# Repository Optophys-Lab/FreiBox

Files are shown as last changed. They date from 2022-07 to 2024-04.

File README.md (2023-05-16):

# FreiBox
Open-ressource for building FreiBox and its modules (including FreiBox Active Commutator).
It contains codes, references tables for electronic components, 3D stl files and pictures.

Contact:
Brice De La Crompe,
brice . de . la . crompe /at/ biologie . uni-freiburg . de,
Optophysiology Lab (Ilka Diester's lab),
Freiburg, Germany

For specific question regarding the GUI, please contact:
megan . j . schneck /at/ gmail . com

______________________
Component Overview
______________________

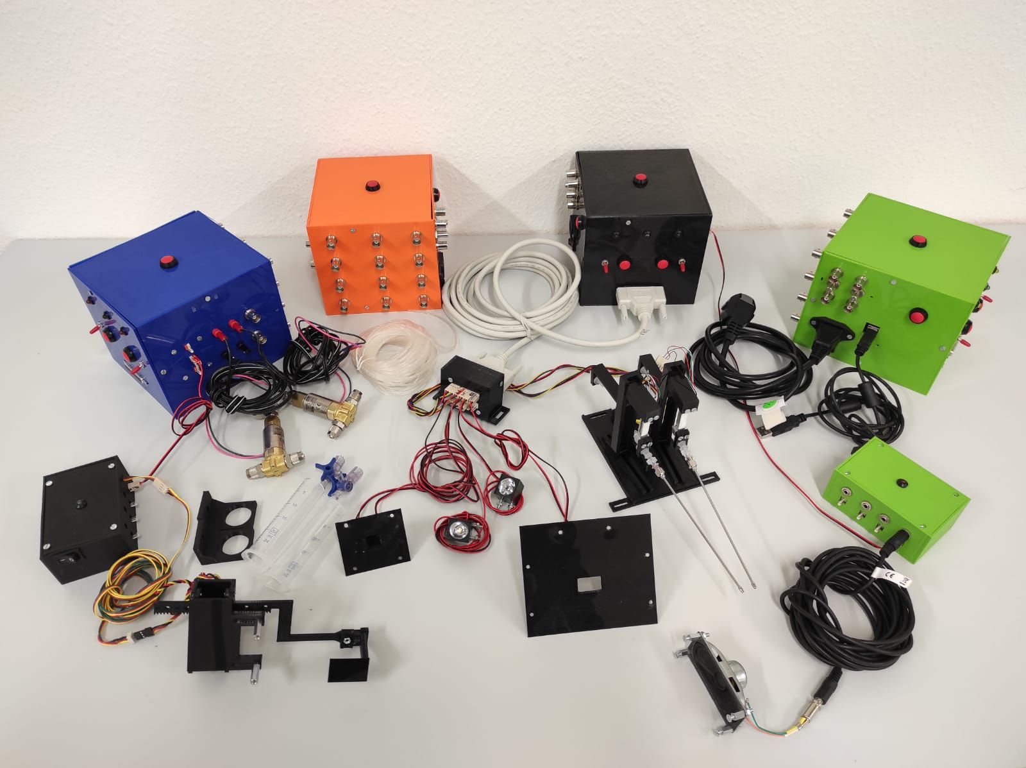
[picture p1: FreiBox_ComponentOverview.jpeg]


______________________
Licking Chamber
______________________

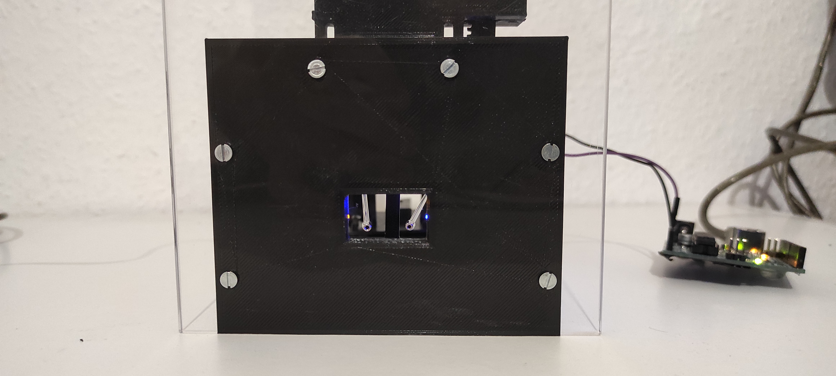
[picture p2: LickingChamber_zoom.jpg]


______________________
Lickometer in action
______________________

LickingRecordingExample_Compressed.mp4

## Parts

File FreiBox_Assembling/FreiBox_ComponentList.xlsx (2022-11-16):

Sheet: Total
Table1: Freibox plateform
ID | Name | Price
1 | Freibox | 902.8118
2 | Commutator | 110.74
3 | Tools | 160.4
4 | Miniscope UCLA v4 | 1580
5 | Open ephys system | 3479
6 | Laser Controler | 900
7 | Computer | 1500
 | Total | 8632.9518
Miniscope UCLA v4
ID | Name | Comment | Quantity | Reference | Supplier | Supplier ref | Price (incl. taxes) | All Price (incl. taxes)
1 | Miniscope V4 Assembly Kit |  | 1 |  | Open ephys |  | 1095 | 1095
2 | New DAQ v3.3 |  | 1 |  | Open ephys |  | 350 | 350
3 | Miniscope V4 Base Plate (Variant 2) |  | 1 |  | Open ephys |  | 35 | 35
4 | Miniscope V4 Coax Cable |  | 1 |  | Open ephys |  | 100 | 100
 |  |  |  |  |  |  | Total | 1580
Open ephys system
ID | Name | Comment | Quantity | Reference | Supplier | Supplier ref | Price (incl. taxes) | All Price (incl. taxes)
1 | Acquisition Board |  | 1 |  | Open ephys |  | 2464 | 2464 | 740
2 | I/O Board |  | 1 |  | Open ephys |  | 85 | 85
3 | RHD 16-channel headstage |  | 1 | Intan/C3334 | Intan |  | 720 | 720
4 | RHD 3-ft (0.9 m) standard SPI interface cable |  | 1 | Intan/C3203 | Intan |  | 210 | 210
 |  |  |  |  |  |  | Total | 3479
Laser Controler
ID | Name | Comment | Quantity | Reference | Supplier | Supplier ref | Price (incl. taxes) | All Price (incl. taxes)
1 | Pulse Pal v2 |  | 1 | Sanworks/1102 |  |  | 900 | 900
 |  |  |  |  |  |  | Total | 900

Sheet: FreiBox
Licking detection |  |  |  |  |  |  |  |  | Categories | Price | Quantities | Total
ID | Name | Comments | Quantity | Reference | Supplier | Supplier ref | Price (incl. taxes) | All Price (incl. taxes) | Licking detection | 44.1 | 2 | 88.2
1 | Strain gauge (load cell, 100G) |  | 2 | SparkFun/SEN-14727 | Digikey | 1568-1898-ND | 12.5 | 25 | Head entry detection | 9.08 | 2 | 18.16
2 | Strain gauge instrumental amplifier |  | 2 | Texas Instruments/INA125PA | Digikey | INA125PA-ND | 7.5 | 15 | Licking signal conditioning | 12.17 | 2 | 24.34
3 | Trimmer 100Ω 0.5W (20 turns) | to set amplifcation gain of the Strain gauge instrumental amplifier | 2 | TTE/67YR100LF | Digikey | 987-1502-ND | 2.05 | 4.1 | Voltage comparator | 3.01 | 4 | 12.04
4 | Ceramic capacitor 100nF |  | 2 | AVX/SR205E104MAR | RS | 144-1933 | 0.5 | 1 | Voltage reference for licking detection module | 40.8 | 2 | 81.6
 |  |  |  |  |  |  |  |  | Voltage reference for Head detection module | 2 | 2 | 4
 |  |  |  |  |  |  | subtotal | 44.1 | Water delivery | 29.86 | 2 | 59.72
 |  |  |  |  |  |  |  |  | Manual water delivery module | 8.58 | 2 | 17.16
Head entry detection |  |  |  |  |  |  |  |  | Light Module | 3.19 | 2 | 6.38
ID | Name | Comments | Quantity | Reference | Supplier | Supplier ref | Price (incl. taxes) | All Price (incl. taxes) | Behavioral Box accessories | 61.1148 | 1 | 61.1148
5 | IR emitting LED |  | 1 | TTE/OP132 | Digikey | 365-1041-ND | 3.25 | 3.25 | Audio pure tone generator | 30.26 | 1 | 30.26
6 | IR receiver phototransistor |  | 1 | Osram/BPX43-4/5 | Digikey | 475-2660-ND | 5.4 | 5.4 | Optoisolated Gate control circuit | 48.55 | 1 | 48.55
7 | Resistor 100Ω ±1% |  | 1 | Vishay/MBB02070C1000FCT00 | RS | 477-7681 | 0.35 | 0.35 | Powering | 45.022 | 1 | 45.022
8 | Resistor 100KΩ ±1% |  | 1 | TE Connectivity/ LR1F100K | RS | 171-1691 | 0.08 | 0.08 | Arduino and accessories | 145.9 | 1 | 145.9
 |  |  |  |  |  |  |  |  | Inside Box | 13.94 | 1 | 13.94
 |  |  |  |  |  |  |  |  | Mechanical parts | 45.04 | 1 | 45.04
 |  |  |  |  |  |  | subtotal | 9.08 | Connectors | 59.9 | 1 | 59.9
 |  |  |  |  |  |  |  |  | Plexiglas box | 77 | 1 | 77
Licking signal conditioning |  |  |  |  |  |  |  |  | 3D printing | 64.485 | 1 | 64.485
ID | Name | Comments | Quantity | Reference | Supplier | Supplier ref | Price (incl. taxes) | All Price (incl. taxes) |  |  | Total | 902.8118
9 | High speed operational amplifier | To divide the licking signal and limit the output to [-5V; +5V] | 2 | Texas Instruments/LM7171BIN/NOPB | Digikey | LM7171BIN/NOPB | 4.8 | 9.6
10 | Resistor 5kΩ ±1% |  | 1 | Vishay/MBB0207VD5001BC100 | Digikey | BC4514CT-ND | 0.75 | 0.75
11 | Resistor 1.5kΩ ±1% |  | 1 | Tru components/1557396 | Conrad | 1557396 - VQ | 0.07 | 0.07
12 | Resistor 100Ω ±1% |  | 1 | Vishay/MBB02070C1000FCT00 | RS | 477-7681 | 0.35 | 0.35
13 | Zener limiting diode (5.1V) | Limiting diode for licking signal divider. Limit output to [-5V; +5V] | 2 | Vishay/BZX85C5V1-TR | Conrad | 180572 | 0.2 | 0.4
14 | Ceramic capacitor 100nF |  | 2 | AVX/SR205E104MAR | RS | 144-1933 | 0.5 | 1
 |  |  |  |  |  |  | subtotal | 12.17
Voltage comparator
ID | Name | Comments | Quantity | Reference | Supplier | Supplier ref | Price (incl. taxes) | All Price (incl. taxes)
15 | Differential comparator |  | 1 | Texas Instruments/LM311P | Digikey | 296-1389-5-ND | 0.65 | 0.65
16 | Ceramic capacitor 2.2nF |  | 1 | Tru components/TC-K2,2NF5 | Conrad | 1589521 | 0.09 | 0.09
17 | Resistor 100Ω ±1% |  | 1 | Vishay/MBB02070C1000FCT00 | RS | 477-7681 | 0.35 | 0.35
18 | Resistor 1MΩ ±1% |  | 1 | Yageo/MF0207F1M0H | Conrad | 1417625 | 0.13 | 0.13
19 | Resistor 470KΩ ±1% |  | 1 | Yageo/MF0207F470KH | Conrad | 1417688 - 62 | 0.04 | 0.04
20 | Resistor 5kΩ ±1% | Pull-up resistor | 1 | Vishay/MBB0207VD5001BC100 | Digikey | BC4514CT-ND | 0.75 | 0.75
21 | Ceramic capacitor 100nF |  | 2 | AVX/SR205E104MAR | RS | 144-1933 | 0.5 | 1
 |  |  |  |  |  |  | subtotal | 3.01
Voltage reference for licking detection module
ID | Name | Comments | Quantity | Reference | Supplier | Supplier ref | Price (incl. taxes) | All Price (incl. taxes)
22 | Precision potentiometer 10KΩ 2W (10 turns) | to set easily the licking detection threshold (V REF) | 2 | Bourns/3590S-2-103L | Digikey | 3590S-2-103L-ND | 20.4 | 40.8
 |  |  |  |  |  |  | subtotal | 40.8
Voltage reference for Head detection module
ID | Name | Comments | Quantity | Reference | Supplier | Supplier ref | Price (incl. taxes) | All Price (incl. taxes)
23 | Trimmer 10kΩ 0.5W (25 turns) |  | 1 | Bourns/PV36W103C01B00 | Digikey | 490-2875-ND | 2 | 2
 |  |  |  |  |  |  | subtotal | 2
Water delivery
ID | Name | Comments | Quantity | Reference | Supplier | Supplier ref | Price (incl. taxes) | All Price (incl. taxes)
24 | Water delivery MOSFET (N-CH 55V) |  | 1 | Infineon Technologies /IRLZ44NPBF | Digikey | IRLZ44NPBF-ND | 1.7 | 1.7
25 | Solenoid Valve (24V) |  | 1 | SMC/VDW250-5G-2-01F-Q | RS | 701-3230 | 27.43 | 27.43
26 | Flyback diode (50V) |  | 1 | Comchip/1N4001-G | Digikey | 641-1310-1-ND | 0.25 | 0.25
27 | Resistor 100Ω ±1% | MOFSET resistor | 1 | Vishay/MBB02070C1000FCT00 | RS | 477-7681 | 0.35 | 0.35
28 | Resistor 100KΩ ±1% |  | 1 | TE Connectivity/ LR1F100K | RS | 171-1691 | 0.08 | 0.08
29 | Blocking diode | To protect Arduino pin from reverse polarity induce by toogle activation | 1 | Vishay/1N4148-TAP | Conrad | 564851 | 0.05 | 0.05
 |  |  |  |  |  |  | subtotal | 29.86
Manual water delivery module
ID | Name | Comments | Quantity | Reference | Supplier | Supplier ref | Price (incl. taxes) | All Price (incl. taxes)
30 | Transistor NPN |  | 1 | ON semiconductor/2N3904BU | Conrad | 163350-VQ | 0.13 | 0.13
31 | Ceramic capacitor 100nF |  | 1 | AVX/SR205E104MAR | RS | 144-1933 | 0.5 | 0.5
32 | Resistor 5kΩ ±1% |  | 1 | Vishay/MBB0207VD5001BC100 | Digikey | BC4514CT-ND | 0.75 | 0.75
33 | Resistor 10kΩ ±1% |  | 1 | Vishay/MBB02070C1002FCT00 | RS | 477-8246 | 0.3 | 0.3
34 | Resistor 100KΩ ±1% |  | 1 | TE Connectivity/ LR1F100K | RS | 171-1691 | 0.08 | 0.08
35 | Toggle switch |  | 1 | Goobay/KNX 1 | Conrad | 701343 - 62 | 1.02 | 1.02
36 | Push button |  | 1 | E-Switch/PV5S24019 | Digikey | EG5952-ND | 5.8 | 5.8
 |  |  |  |  |  |  | subtotal | 8.58
Light Module
ID | Name | Comments | Quantity | Reference | Supplier | Supplier ref | Price (incl. taxes) | All Price (incl. taxes)
37 | LED house light |  | 2 | Nichia/NSPL500DS | Conrad | 181251 - 62 | 1.01 | 2.02
38 | Transistor NPN |  | 4 | ON semiconductor/2N3904BU | Conrad | 163350-VQ | 0.13 | 0.52
39 | Resistor 100Ω ±1% |  | 1 | Vishay/MBB02070C1000FCT00 | RS | 477-7681 | 0.35 | 0.35
40 | Resistor 10kΩ ±1% |  | 1 | Vishay/MBB02070C1002FCT00 | RS | 477-8246 | 0.3 | 0.3
 |  |  |  |  |  |  | subtotal | 3.19
Behavioral Box accessories
ID | Name | Comments | Quantity | Reference | Supplier | Supplier ref | Price (incl. taxes) | All Price (incl. taxes)
41 | LED reflector |  | 2 | Mentor/2451.5100 | Conrad | 149502 - 62 | 0.64 | 1.28
42 | Optical Grade Plastic Optical Fiber Unjacketed | To relay IR light in the licking chamber and nose poke | 1 | Edmund Optics | Edmund Optics | 02-534 | 1.6 | 1.6
43 | Licking spout, stainless steel cannula (2,00x120mm lg, end shape olive B) |  | 2 | Acufirm/1464 LL | Acufirm |  | 17.46 | 34.92
44 | Licking spout luer connectors (Rotilabo) | To connect the licking spour to the strain gauge | 2 | Carl Roth/CT68.1 | Carl Roth |  | 1.7 | 3.4
45 | Female luer Bulkhead 1/4-28 UNF Thread, to 1/162" hose Barb |  | 4 | Masterflex/45508-30 | Fisher | 15253265 | 1.0612 | 4.2448
46 | Tubing, Tygon® (E-3603) |  | 1 | Saint Gobain/5205536 | Omnilab | 5205536 | 15.67 | 15.67
 |  |  |  |  |  |  | subtotal | 61.1148
Audio pure tone generator
ID | Name | Comments | Quantity | Reference | Supplier | Supplier ref | Price (incl. taxes) | All Price (incl. taxes)
47 | Audio amplifier (class D, 2.5W) |  | 1 | Adafruit/2130 | Digikey | 1528-1492-ND | 4.4 | 4.4
48 | SPEAKER 8Ω 2W |  | 1 | PUI Audio / AS07008PO-2-R | Digikey | 668-1191-ND | 4.55 | 4.55
49 | Optoisolator |  | 1 | Broadcom/HCPL-2200-000E | RS | 547-3908 | 4.88 | 4.88
50 | Transistor NPN |  | 6 | ON semiconductor/2N3904BU | Conrad | 163350-VQ | 0.13 | 0.78
51 | Resistor 1.6KΩ ±1% |  | 1 | TE Connectivity/LR1F1K6 | RS | 148-556 | 0.17 | 0.17
52 | Resistor 100Ω ±1% |  | 2 | Vishay/MBB02070C1000FCT00 | RS | 477-7681 | 0.35 | 0.7
53 | Ceramic capacitor 100nF |  | 1 | AVX/SR205E104MAR | RS | 144-1933 | 0.5 | 0.5
54 | Jack cable 3,5mm, 5.00 m |  | 1 | SpeaKa Professional /SP-7870376 | Conrad | 1967594 | 6.5 | 6.5
55 | Panel Mount 3,5mm Jack Socket |  | 2 | Conrad/734136 | Conrad | 734136 | 1.39 | 2.78
56 | Power supply 5V |  | 1 | local provider |  |  | 5 | 5
 |  |  |  |  |  |  | subtotal | 30.26
Optoisolated Gate control circuit
ID | Name | Comments | Quantity | Reference | Supplier | Supplier ref | Price (incl. taxes) | All Price (incl. taxes)
57 | Gate Servo motor |  | 1 | Hitec/HS-645MG | Conrad | 209899 | 38 | 38
58 | Optoisolator |  | 1 | Broadcom/HCPL-2200-000E | RS | 547-3908 | 4.88 | 4.88
59 | Resistor 1.6KΩ ±1% |  | 1 | TE Connectivity/LR1F1K6 | RS | 148-556 | 0.17 | 0.17
60 | Ceramic capacitor 100nF |  | 1 | AVX/SR205E104MAR | RS | 144-1933 | 0.5 | 0.5
61 | Power supply 5V |  | 1 | local provider |  |  | 5 | 5
 |  |  |  |  |  |  | subtotal | 48.55
Powering
ID | Name | Comments | Quantity | Reference | Supplier | Supplier ref | Price (incl. taxes) | All Price (incl. taxes)
62 | Power supply, AC/DC Converter, 5V/12V/24V/-12V |  | 1 | Mean Well/RQ-50D | Digikey | 1866-4115-ND | 31 | 31
63 | Electrolytic capacitor 100µF |  | 4 | NIC/JL101M50V8x11.5F | RS | 737-3936 | 0.198 | 0.792
64 | Power cable | connection type: IEC 320-C13 | 1 | Phihong USA/AC30UEU | Digikey | 993-1038-ND | 6.27 | 6.27
65 | Power plug, mount panel | IEC connector | 1 | Tru components/781/SW | Conrad | 1567149 | 1.29 | 1.29
66 | Power toggle switch |  | 3 | Tru components/1587515 | Conrad | 1587515 | 1.89 | 5.67
 |  |  |  |  |  |  | subtotal | 45.022
Arduino and accessories
ID | Name | Comments | Quantity | Reference | Supplier | Supplier ref | Price (incl. taxes) | All Price (incl. taxes)
67 | Arduino MEGA (ATMEGA2560) |  | 1 | Arduino/A000067 | Digikey | 1050-1018-ND | 44.75 | 44.75
68 | SHIELD - MEGA PROTO PCB REV3 |  | 1 | Arduino/A000080 | Digikey | 1050-1030-ND | 5.55 | 5.55
69 | Perforated Prototype Boards, 2.54mm (78 x 58 mm) |  | 10 | DFRobot/FIT0099 | Digikey | 1738-1000-ND | 1.7 | 17
70 | 22AWG colored cable |  | 1 | Adafruit/3174 | Digikey | 1528-1745-ND | 33.25 | 33.25
71 | 50Ω BNC Connector, Straight, Panel Mount |  | 10 | TE Connectivity/5-1634523-1 | RS | 512-1174 | 3.02 | 30.2
72 | LED Holder for Through-Hole 5mm LED |  | 3 | Kingbright/RTF-5020 | RS | 262-3009 | 0.75 | 2.25
73 | Red LED 5mm | Water delivery LED | 10 | Kingbright/L-57IID | RS | 228-5821 | 0.4 | 4
74 | Green LED 5mm | Power LED | 10 | Kingbright/L-53SGD | RS | 247-1678 | 0.35 | 3.5
75 | Resistor 120Ω ±5% | Resistor for LED | 20 | RS PRO/707-7599 | RS | 707-7599 | 0.27 | 5.4
 |  |  |  |  |  |  | subtotal | 145.9
Inside Box
ID | Name | Comments | Quantity | Reference | Supplier | Supplier ref | Price (incl. taxes) | All Price (incl. taxes)
76 | Perforated Prototype Boards, 2.54mm (44.5 x 33 mm) |  | 1 | Chip Quik/SBBTH1512-1 | Digikey | SBBTH1512-1-ND | 3 | 3
77 | D-SUB 25 male plug |  | 1 | Connfly/DS1033-25MBNSISS | Conrad | 1389980 | 0.45 | 0.45
78 | D-SUB 25 cable 5m, male/female |  | 1 | Digitus/AK-610201-050-E | Conrad | 972302 | 9.99 | 9.99
79 | D-SUB 25 female plug |  | 1 | Connfly/DS1033-25FBNSISS-CT | Conrad | 1389965 | 0.5 | 0.5
 |  |  |  |  |  |  | subtotal | 13.94
Mechanical parts
ID | Name |  | Quantity | Reference | Supplier | Supplier ref | Price (incl. taxes) | All Price (incl. taxes)
80 | Hex Standoff Male/Female, 30mm, M3xM3 | to hold the electronic cards | 10 | RS PRO | RS | 806-6617 | 0.35 | 3.5
81 | Hex Standoff Male/Female, 20mm, M3xM3 | to hold the motor | 2 | RS PRO | RS | 806-6613 | 0.27 | 0.54
82 | Hex Standoff Male/Female, 10mm, M3xM3 | For holding the speaker | 4 | RS PRO | RS | 806-6588 | 0.19 | 0.76
83 | Hex Standoff Male/Male, 5mm, M3xM3 |  | 50 | RS PRO | RS | 806-6601 | 0.17 | 8.5
84 | Hex Nut, M3 | Pack 250 | 1 | RS PRO | RS | 560-293 | 5.71 | 5.71
85 | M3, length 30mm (Countersunk Head) | Pack 100 | 1 | RS PRO | RS | 914-1658 | 10.1 | 10.1
86 | M3, length 16mm (Countersunk Head) | Pack 100 | 1 | RS PRO | RS | 908-7371 | 3.43 | 3.43
87 | M3, length 12mm (Countersunk Head) | Pack 100 | 1 | RS PRO | RS | 528-952 | 8.9 | 8.9
88 | M3, length 8mm (Countersunk Head) | Pack 100 | 1 | RS PRO | RS | 908-7481 | 3.6 | 3.6
 |  |  |  |  |  |  | subtotal | 45.04
Connectors
ID | Name | Comments | Quantity | Reference | Supplier | Supplier ref | Price (incl. taxes) | All Price (incl. taxes)
89 | WR-WTB Female Connector, 2.54mm pitch, 2 pins |  | 15 | Wurth Elektronik/61900211621 | RS | 828-1468 | 0.14 | 2.1
90 | WR-WTB Female Connector, 2,54mm pitch, 3 pins |  | 10 | Wurth Elektronik/61900311621 | RS | 828-1478 | 0.16 | 1.6
91 | WR-WTB Female Connector, 2,54mm pitch, 4 pins |  | 15 | Wurth Elektronik/61900411621 | RS | 828-1493 | 0.31 | 4.65
92 | WR-WTB Female Connector, 2,54mm pitch, 5 pins |  | 5 | Wurth Elektronik/61900511621 | RS | 828-1503 | 0.21 | 1.05
93 | WR-WTB Female Crimp Terminal Contact 22AWG |  | 50 | Wurth Elektronik/61900113722DEC | RS | 828-1452 | 0.18 | 9
94 | WR-WTB Pin Header, Right Angle, 2.54mm, 2 pins |  | 15 | Wurth Elektronik/61900211021 | RS | 828-1456 | 0.65 | 9.75
95 | WR-WTB Pin Header, Right Angle, 2.54mm, 3 pins |  | 10 | Wurth Elektronik/61900311021 | RS | 828-1471 | 0.85 | 8.5
96 | WR-WTB Pin Header, Right Angle, 2.54mm, 4 pins |  | 15 | Wurth Elektronik/61900411021 | RS | 828-1480 | 1.1 | 16.5
97 | WR-WTB Pin Header, Right Angle, 2.54mm, 5 pins |  | 5 | Wurth Elektronik/61900511021 | RS | 828-1490 | 1.35 | 6.75
 |  |  |  |  |  |  | subtotal | 59.9
Plexiglas box
ID | Name |  | Quantity | Reference | Supplier | Supplier ref | Price (incl. taxes) | All Price (incl. taxes)
98 | Plexiglas box (40x15x25cm), 4 walls and the floor plexiglass (75x35x0.8cm) |  | 1 |  | Express Zuschnitt |  | 66 | 66
99 | Acrifix 192 Acrylglaskleber 539813 100 g |  | 1 |  | Conrad | 539813 - VQ | 11 | 11
 |  |  |  |  |  |  | subtotal | 77
3D printing
ID | Name |  | Quantity | Reference | Supplier | Supplier ref | Price (incl. taxes) | All Price (incl. taxes)
100 | Filament PLA 2.85 mm 750 g |  | 1.5 | Ultimaker/PLA - M0751 Black 750 - 211399 | Conrad | 1528665 - 62 | 42.99 | 64.485
 |  |  |  |  |  |  | subtotal | 64.485

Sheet: Commutator
Commutator
ID | Name | Comments | Quantity | Reference | Supplier | Supplier ref | Price (incl. taxes) | All Price (incl. taxes)
1 | Hall Effect Senso |  | 3 | TDK-Micronas/HAL835UT-A | Digikey | HAL835UT-ACT-ND | 3.3 | 9.9
2 | Stepper motor Nema17 |  | 1 | Joy-it/Nema17-04 | Conrad | 2148834 | 16 | 16
3 | Arduino Uno Rev3 |  | 1 | Arduino/A000073 | Conrad | 191789 - 62 | 23 | 23
4 | Stepper motor driver A4988 |  | 1 | Qita/MO03018 | Conrad | 802287605 - 62 | 5.95 | 5.95
5 | Slip Ring, 12 wires |  | 1 | Adafruit/1196 | Digikey | 1528-1176-ND | 22.14 | 22.14
6 | Power supply 12V |  | 1 | HN-Power/HNP06-UNI | Conrad | 2161762 | 11 | 11
7 | Hex Standoff Male/Female, 30mm, M3xM3 | to hold the electronic cards | 2 | RS PRO | RS | 806-6617 | 0.35 | 0.7
8 | M3, length 8mm (Countersunk Head) | Pack of 100 | 1 | RS PRO | RS | 908-7481 | 3.6 | 3.6
9 | M3, length 16mm (Countersunk Head) | Pack of 100 | 1 | RS PRO | RS | 908-7371 | 3.45 | 3.45
10 | Epoxy glue 2 components |  | 1 | UHU/45700 | Conrad | 478703 | 14 | 14
11 | Magnet, Neodymium 8mm (Dia.) x 3mm |  | 1 |  | Amazon |  | 1 | 1
 |  |  |  | 2015699-1 | Digikey
 |  |  |  |  |  |  | Total | 110.74

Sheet: Tools
Tools
ID | Name | Quantity | Reference | Supplier | Supplier ref | Price (incl. taxes) | All Price (incl. taxes)
1 | Soldering station | 1 | BaseTech/BT-2147832 | Conrad | 2147832 - VQ | 40 | 40
2 | Crimper | 1 | Basetech/BT-1762766 | Conrad | 1762766 | 12 | 12
3 | Wire stripper | 1 | Weicon/51000005 | Conrad | 804037 | 19 | 19
4 | Desoldering pump | 1 | Toolcraft/ZD-190 | Conrad | 2253839 | 5.9 | 5.9
5 | Precision cutter plier | 1 | Toolcraft/816744 | Conrad | 816744 | 12 | 12
6 | Screwdriver sets | 1 | Mannesmann/96058C | Conrad | 801950 | 9.5 | 9.5
7 | Plier | 1 | Donau/3536 | Conrad | 817726 - 62 | 5 | 5
8 | Dremel | 1 | Dremel/F0133000JA | Conrad | 817680 | 57 | 57
 |  |  |  |  |  | Total | 160.4

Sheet: 3D printed parts
ID | Box Parts | Parameters |  | Individual parts |  |  |  | Final parts |  |  |  | Comments
 |  | Layer height | Infill | time | time (hh:mm:ss) | g | m | Qty | time (hh:mm:ss) | g | m
1 | Freibox_InsideBox_Jan2021_FrontPart | 0.2 | 20 | 1h52min | 1:52:00 | 23 | 2.89 | 1 | 1:52:00 | 23 | 2.89
2 | Freibox_InsideBox_Jan2021_Rear | 0.2 | 20 | 38min | 0:38:00 | 6 | 0.78 | 1 | 0:38:00 | 6 | 0.78
3 | Freibox_LEDholder_Jan2021_Part1 | 0.2 | 20 | 16min | 0:16:00 | 3 | 0.35 | 1 | 0:16:00 | 3 | 0.35
4 | Freibox_LEDholder_Jan2021_Part2 | 0.2 | 20 | 17min | 0:17:00 | 3 | 0.34 | 1 | 0:17:00 | 3 | 0.34
5 | Freibox_LickingChamber_Jan2021_MotorGear | 0.2 | 20 | 20min | 0:20:00 | 3 | 0.33 | 1 | 0:20:00 | 3 | 0.33
6 | Freibox_LickingChamberGate_Jan2021_gate | 0.2 | 20 | 24min | 0:24:00 | 4 | 0.47 | 1 | 0:24:00 | 4 | 0.47 | support
7 | Freibox_LickingChamberGate_Jan2021_gateSlider | 0.2 | 20 | 36min | 0:36:00 | 5 | 0.64 | 1 | 0:36:00 | 5 | 0.64
8 | Freibox_LickingChamberGate_Jan2021_LickingChamber | 0.2 | 20 | 1h21min | 1:21:00 | 14 | 1.74 | 11 | 14:51:00 | 154 | 19.14
9 | Freibox_LickingChamberGate_Jan2021_motorHolder_Part1 | 0.2 | 20 | 1h06min | 1:06:00 | 11 | 1.4 | 1 | 1:06:00 | 11 | 1.4
10 | Freibox_LickingChamberGate_Jan2021_motorHolder_Part2 | 0.2 | 20 | 52min | 0:52:00 | 9 | 1.12 | 1 | 0:52:00 | 9 | 1.12
11 | Freibox_LickingSpoutHolder_Jan2021_lickingSpoutHolder | 0.2 | 20 | 7min | 0:07:00 | 1 | 0.13 | 2 | 0:14:00 | 2 | 0.26
12 | Freibox_LickingSpoutHolder_Jan2021_pipeSecuringConnector | 0.2 | 20 | 21min | 0:21:00 | 4 | 0.46 | 2 | 0:42:00 | 8 | 0.92
13 | Freibox_LickingSpoutHolder_Jan2021_Plateforme_Part1 | 0.2 | 20 | 2h38 | 2:38:00 | 31 | 3.88 | 1 | 2:38:00 | 31 | 3.88
14 | Freibox_LickingSpoutHolder_Jan2021_Plateforme_Part2 | 0.2 | 20 | 1h56 | 1:56:00 | 21 | 2.64 | 1 | 1:56:00 | 21 | 2.64
15 | Freibox_LickingSpoutHolder_Jan2021_slidingTour | 0.2 | 20 | 58min | 0:58:00 | 11 | 1.45 | 2 | 1:56:00 | 22 | 2.9
16 | Freibox_LickingSpoutHolder_Jan2021_strainGaugeHolder | 0.2 | 20 | 30min | 0:30:00 | 5 | 0.63 | 2 | 1:00:00 | 10 | 1.26
17 | Freibox_NosePokePort_Jan2021 | 0.2 | 20 | 42min | 0:42:00 | 7 | 0.93 | 1 | 0:42:00 | 7 | 0.93
18 | Freibox_SyringeHolder_Jan2021 | 0.2 | 20 | 34min | 0:34:00 | 7 | 0.84 | 2 | 1:08:00 | 14 | 1.68
19 | Freibox_ArduinoHolder_Part1_Jan2021 | 0.2 | 20 | 1h20min | 1:20:00 | 12 | 1.58 | 1 | 1:20:00 | 12 | 1.58
20 | Freibox_ArduinoHolder_Part2_Jan2021 | 0.2 | 20 | 38min | 0:38:00 | 7 | 0.89 | 1 | 0:38:00 | 7 | 0.89
21 | Freibox_ElectronicBox_jan2021_Front | 0.2 | 20 | 4h23min | 4:23:00 | 49 | 6.16 | 1 | 4:23:00 | 49 | 6.16
22 | Freibox_ElectronicBox_jan2021_Ground | 0.2 | 20 | 5h16min | 5:16:00 | 63 | 8 | 1 | 5:16:00 | 63 | 8
23 | Freibox_ElectronicBox_jan2021_Left | 0.2 | 20 | 4h31min | 4:31:00 | 51 | 6.4 | 1 | 4:31:00 | 51 | 6.4
24 | Freibox_ElectronicBox_jan2021_Rear | 0.2 | 20 | 4h25min | 4:25:00 | 49 | 6.17 | 1 | 4:25:00 | 49 | 6.17
25 | Freibox_ElectronicBox_jan2021_Right | 0.2 | 20 | 4h22min | 4:22:00 | 48 | 6.12 | 1 | 4:22:00 | 48 | 6.12
26 | Freibox_ElectronicBox_jan2021_top | 0.2 | 20 | 4h41min | 4:41:00 | 52 | 6.55 | 1 | 4:41:00 | 52 | 6.55
27 | Freibox_AuditoryBox_Jan2021_Part1 | 0.2 | 20 | 4h22min | 4:22:00 | 50 | 6.29 | 1 | 4:22:00 | 50 | 6.29
28 | Freibox_AuditoryBox_Jan2021_Part2 | 0.2 | 20 | 1h06 | 1:06:00 | 12 | 1.54 | 1 | 1:06:00 | 12 | 1.54
 |  |  |  |  |  |  |  |  | 66:32:00 | 729 | 91.63
ID | Commutator Parts | Parameters |  | Individual parts |  |  |  | Final parts |  |  |  | Comments
 |  | Layer height | Infill | time | time (hh:mm:ss) | g | m | Qty | time (hh:mm:ss) | g | m
1 | MiniscopeCommutator_NemaDesign_Jan2021_Based | 0.2 | 20 | 2h13min | 2:13:00 | 29 | 3.72 | 1 | 2:13:00 | 29 | 3.72
2 | MiniscopeCommutator_NemaDesign_Jan2021_Blocker | 0.2 | 20 | 1h14min | 1:14:00 | 14 | 1.72 | 1 | 1:14:00 | 14 | 1.72
3 | MiniscopeCommutator_NemaDesign_Jan2021_DetectorRing | 0.2 | 20 | 1h | 1:00:00 | 6 | 0.75 | 1 | 1:00:00 | 6 | 0.75
4 | MiniscopeCommutator_NemaDesign_Jan2021_Linker | 0.2 | 20 | 7min | 0:07:00 | 1 | 0.08 | 1 | 0:07:00 | 1 | 0.08
5 | MiniscopeCommutator_NemaDesign_Jan2021_MagnetBall_Part1 | 0.2 | 20 | 4min | 0:04:00 | 1 | 0.08 | 1 | 0:04:00 | 1 | 0.08
6 | MiniscopeCommutator_NemaDesign_Jan2021_MagnetBall_Part2 | 0.2 | 20 | 4min | 0:04:00 | 1 | 0.07 | 1 | 0:04:00 | 1 | 0.07
7 | MiniscopeCommutator_NemaDesign_Jan2021_MotorGear | 0.2 | 20 | 1h01min | 1:01:00 | 11 | 1.34 | 1 | 1:01:00 | 11 | 1.34
8 | MiniscopeCommutator_NemaDesign_Jan2021_SlipRingGear | 0.2 | 20 | 1h01min | 1:01:00 | 11 | 1.34 | 1 | 1:01:00 | 11 | 1.34
 |  |  |  |  |  |  |  |  | 6:44:00 | 74 | 9.1

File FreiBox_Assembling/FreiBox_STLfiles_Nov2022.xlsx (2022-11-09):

ID | Box Parts | Parameters |  | Individual parts |  |  |  | Final parts |  |  |  | Comments
 |  | Layer height | Infill | time | time (hh:mm:ss) | g | m | Qty | time (hh:mm:ss) | g | m
1 | Freibox_InsideBox_FrontPart | 0.2 | 20 | 1h52min | 1:52:00 | 23 | 2.89 | 1 | 1:52:00 | 23 | 2.89
2 | Freibox_InsideBox_Rear | 0.2 | 20 | 38min | 0:38:00 | 6 | 0.78 | 1 | 0:38:00 | 6 | 0.78
3 | Freibox_LEDholder_Part1 | 0.2 | 20 | 16min | 0:16:00 | 3 | 0.35 | 1 | 0:16:00 | 3 | 0.35
4 | Freibox_LEDholder_Part2 | 0.2 | 20 | 17min | 0:17:00 | 3 | 0.34 | 1 | 0:17:00 | 3 | 0.34
5 | Freibox_LickingChamber_MotorGear | 0.2 | 20 | 20min | 0:20:00 | 3 | 0.33 | 1 | 0:20:00 | 3 | 0.33
6 | Freibox_LickingChamber_gate | 0.2 | 20 | 24min | 0:24:00 | 4 | 0.47 | 1 | 0:24:00 | 4 | 0.47 | support
7 | Freibox_LickingChamber_gateSlider | 0.2 | 20 | 36min | 0:36:00 | 5 | 0.64 | 1 | 0:36:00 | 5 | 0.64
8 | Freibox_LickingChamber_LickingChamber | 0.2 | 20 | 1h21min | 1:21:00 | 14 | 1.74 | 11 | 14:51:00 | 154 | 19.14
9 | Freibox_LickingChamber_motorHolder_Part1 | 0.2 | 20 | 1h06min | 1:06:00 | 11 | 1.4 | 1 | 1:06:00 | 11 | 1.4
10 | Freibox_LickingChamber_motorHolder_Part2 | 0.2 | 20 | 52min | 0:52:00 | 9 | 1.12 | 1 | 0:52:00 | 9 | 1.12
11 | Freibox_LickingSpoutHolder_lickingSpoutHolder | 0.2 | 20 | 7min | 0:07:00 | 1 | 0.13 | 2 | 0:14:00 | 2 | 0.26
12 | Freibox_LickingSpoutHolder_pipeSecuringConnector | 0.2 | 20 | 21min | 0:21:00 | 4 | 0.46 | 2 | 0:42:00 | 8 | 0.92
13 | Freibox_LickingSpoutHolder_Plateforme_Part1 | 0.2 | 20 | 2h38 | 2:38:00 | 31 | 3.88 | 1 | 2:38:00 | 31 | 3.88
14 | Freibox_LickingSpoutHolder_Plateforme_Part2 | 0.2 | 20 | 1h56 | 1:56:00 | 21 | 2.64 | 1 | 1:56:00 | 21 | 2.64
15 | Freibox_LickingSpoutHolder_slidingTour | 0.2 | 20 | 58min | 0:58:00 | 11 | 1.45 | 2 | 1:56:00 | 22 | 2.9
16 | Freibox_LickingSpoutHolder_strainGaugeHolder | 0.2 | 20 | 30min | 0:30:00 | 5 | 0.63 | 2 | 1:00:00 | 10 | 1.26
17 | Freibox_NosePokePort | 0.2 | 20 | 42min | 0:42:00 | 7 | 0.93 | 1 | 0:42:00 | 7 | 0.93
18 | Freibox_SyringeHolder | 0.2 | 20 | 34min | 0:34:00 | 7 | 0.84 | 2 | 1:08:00 | 14 | 1.68
19 | Freibox_ArduinoHolder_Part1 | 0.2 | 20 | 1h20min | 1:20:00 | 12 | 1.58 | 1 | 1:20:00 | 12 | 1.58
20 | Freibox_ArduinoHolder_Part2 | 0.2 | 20 | 38min | 0:38:00 | 7 | 0.89 | 1 | 0:38:00 | 7 | 0.89
21 | Freibox_ElectronicBox_Front | 0.2 | 20 | 4h23min | 4:23:00 | 49 | 6.16 | 1 | 4:23:00 | 49 | 6.16
22 | Freibox_ElectronicBox_Ground | 0.2 | 20 | 5h16min | 5:16:00 | 63 | 8 | 1 | 5:16:00 | 63 | 8
23 | Freibox_ElectronicBox_Left | 0.2 | 20 | 4h31min | 4:31:00 | 51 | 6.4 | 1 | 4:31:00 | 51 | 6.4
24 | Freibox_ElectronicBox_Rear | 0.2 | 20 | 4h25min | 4:25:00 | 49 | 6.17 | 1 | 4:25:00 | 49 | 6.17
25 | Freibox_ElectronicBox_Right | 0.2 | 20 | 4h22min | 4:22:00 | 48 | 6.12 | 1 | 4:22:00 | 48 | 6.12
26 | Freibox_ElectronicBox_top | 0.2 | 20 | 4h41min | 4:41:00 | 52 | 6.55 | 1 | 4:41:00 | 52 | 6.55
27 | Freibox_AuditoryBox_Part1 | 0.2 | 20 | 4h22min | 4:22:00 | 50 | 6.29 | 1 | 4:22:00 | 50 | 6.29
28 | Freibox_AuditoryBox_Part2 | 0.2 | 20 | 1h06 | 1:06:00 | 12 | 1.54 | 1 | 1:06:00 | 12 | 1.54
 |  |  |  |  |  |  |  |  | 66:32:00 | 729 | 91.63
ID | Commutator Parts | Parameters |  | Individual parts |  |  |  | Final parts |  |  |  | Comments
 |  | Layer height | Infill | time | time (hh:mm:ss) | g | m | Qty | time (hh:mm:ss) | g | m
1 | FreiBox_Commutator_Design_v1_Based | 0.2 | 20 | 2h13min | 2:13:00 | 29 | 3.72 | 1 | 2:13:00 | 29 | 3.72
2 | FreiBox_Commutator_Design_v1_Blocker | 0.2 | 20 | 1h14min | 1:14:00 | 14 | 1.72 | 1 | 1:14:00 | 14 | 1.72
3 | FreiBox_Commutator_Design_v1_DetectorRing | 0.2 | 20 | 1h | 1:00:00 | 6 | 0.75 | 1 | 1:00:00 | 6 | 0.75
4 | FreiBox_Commutator_Design_v1_Linker | 0.2 | 20 | 7min | 0:07:00 | 1 | 0.08 | 1 | 0:07:00 | 1 | 0.08
5 | FreiBox_Commutator_Design_v1_MagnetBall_Part1 | 0.2 | 20 | 4min | 0:04:00 | 1 | 0.08 | 1 | 0:04:00 | 1 | 0.08
6 | FreiBox_Commutator_Design_v1_MagnetBall_Part2 | 0.2 | 20 | 4min | 0:04:00 | 1 | 0.07 | 1 | 0:04:00 | 1 | 0.07
7 | FreiBox_Commutator_Design_v1_MotorGear | 0.2 | 20 | 1h01min | 1:01:00 | 11 | 1.34 | 1 | 1:01:00 | 11 | 1.34
8 | FreiBox_Commutator_Design_v1_SlipRingGear | 0.2 | 20 | 1h01min | 1:01:00 | 11 | 1.34 | 1 | 1:01:00 | 11 | 1.34
 |  |  |  |  |  |  |  |  | 6:44:00 | 74 | 9.1

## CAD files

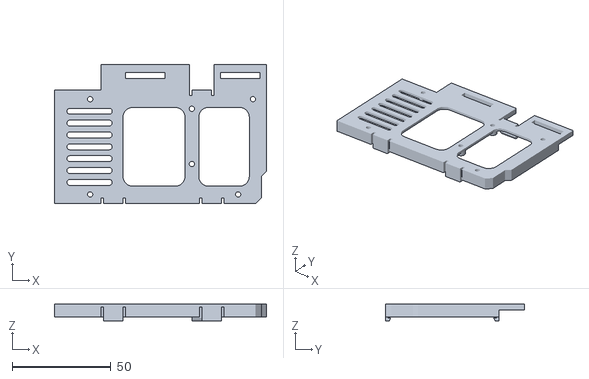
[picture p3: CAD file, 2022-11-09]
FreiBox_Assembling/STLfiles/ArduinoHolder/Freibox_ArduinoHolder_Part1.stl
107.6 x 70.5 x 8.38

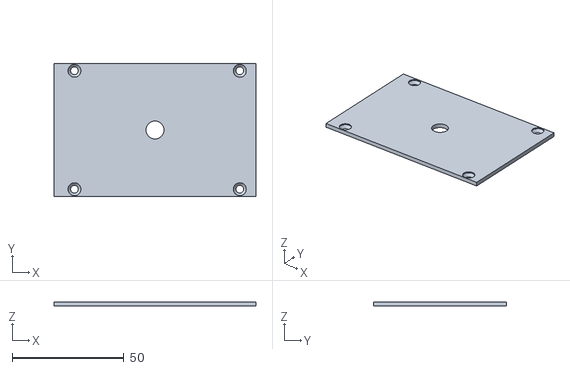
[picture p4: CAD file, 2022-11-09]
FreiBox_Assembling/STLfiles/AuditoryBox/Freibox_AuditoryBox_Part2.stl
90.4 x 59.4 x 2.00

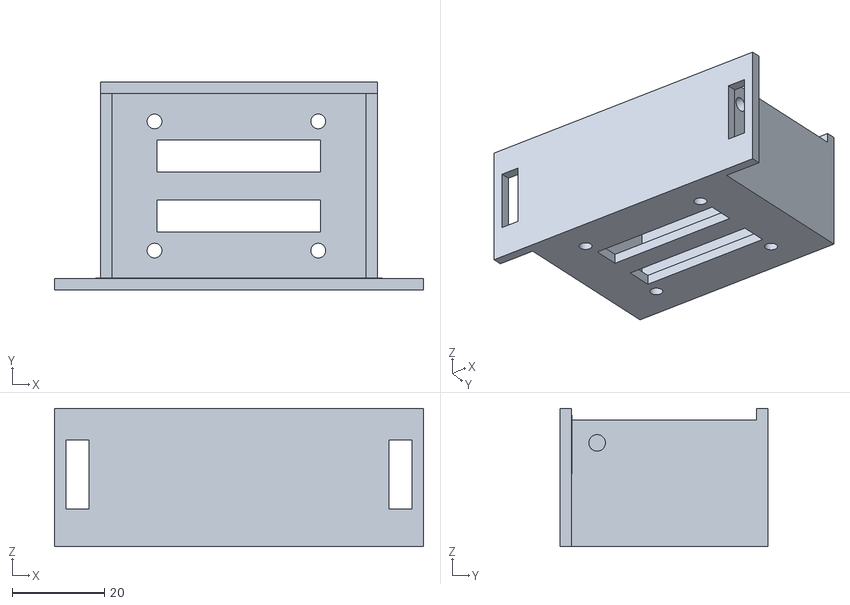
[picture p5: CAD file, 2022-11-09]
FreiBox_Assembling/STLfiles/CableBox/Freibox_InsideBox_FrontPart.stl
80.0 x 45.0 x 30.0

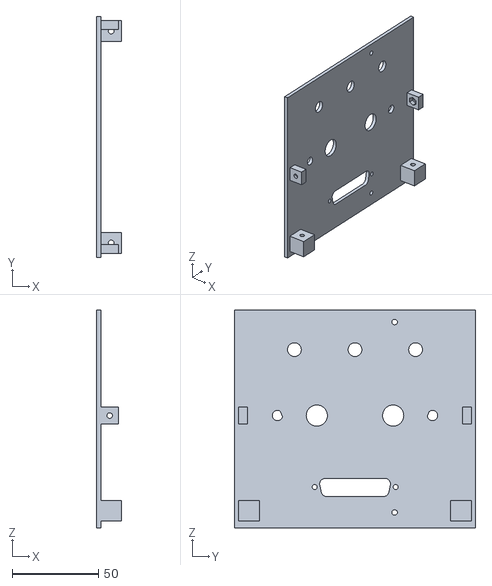
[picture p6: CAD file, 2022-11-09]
FreiBox_Assembling/STLfiles/ElectronicBox/Freibox_ElectronicBox_Front.stl
14.5 x 140.0 x 126.5

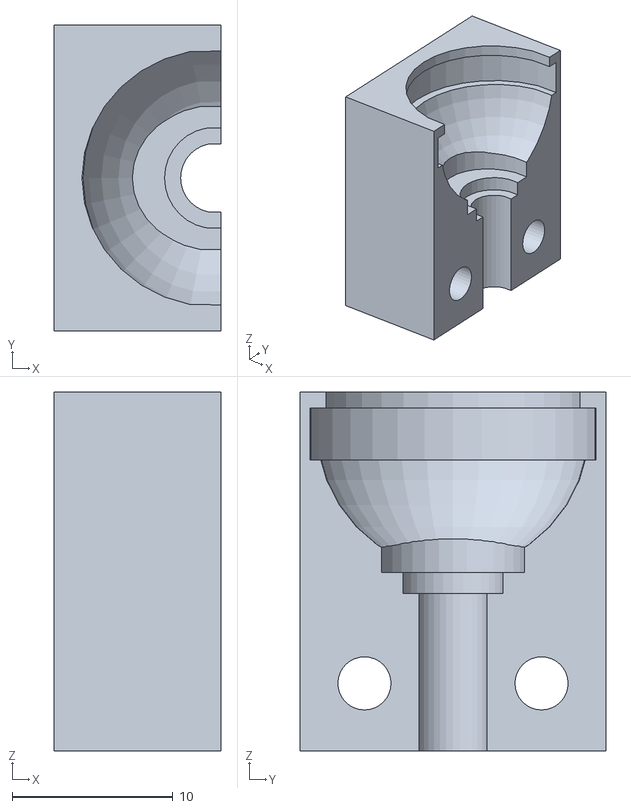
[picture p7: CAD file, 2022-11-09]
FreiBox_Assembling/STLfiles/LEDholder/Freibox_LEDholder_Part1.stl
10.4 x 19.0 x 22.3

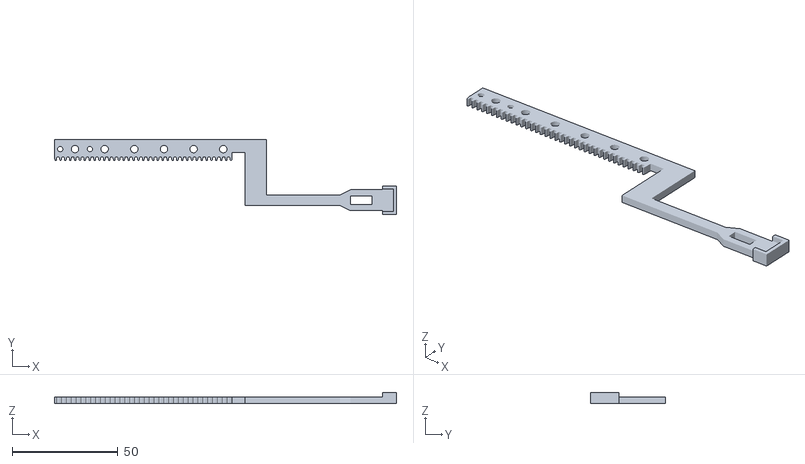
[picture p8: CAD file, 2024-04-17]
FreiBox_Assembling/STLfiles/LickingChamber/Freibox_LickingChamberGate_gateSlider.stl
161.5 x 35.3 x 5.00

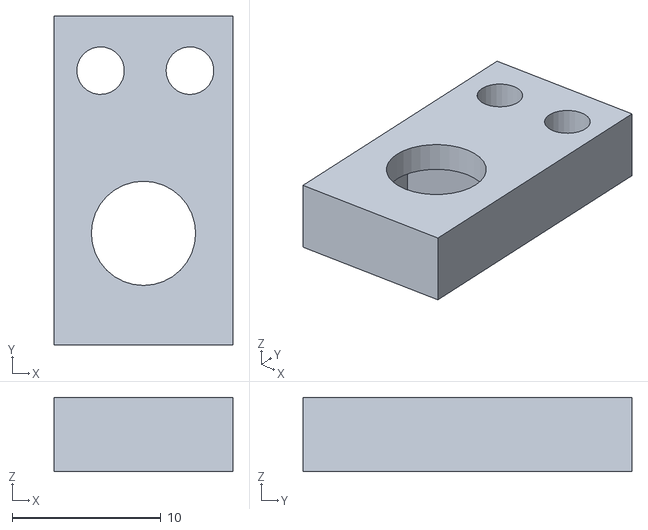
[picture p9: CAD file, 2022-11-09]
FreiBox_Assembling/STLfiles/LickingSpoutHolder/Freibox_LickingSpoutHolder_lickingSpoutHolder.stl
12.0 x 22.1 x 5.00

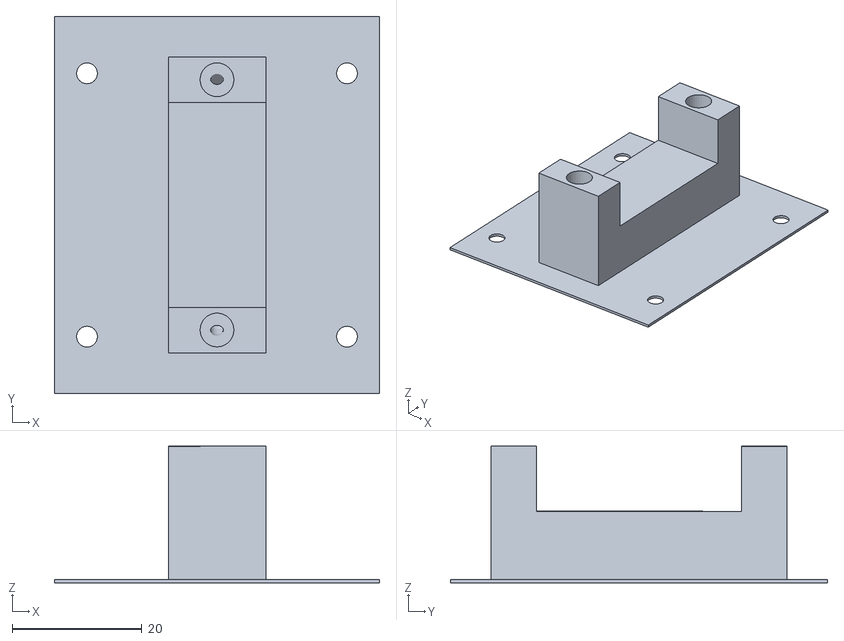
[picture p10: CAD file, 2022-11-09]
FreiBox_Assembling/STLfiles/NosePoke/Freibox_NosePokePort.stl
50.0 x 58.0 x 21.0

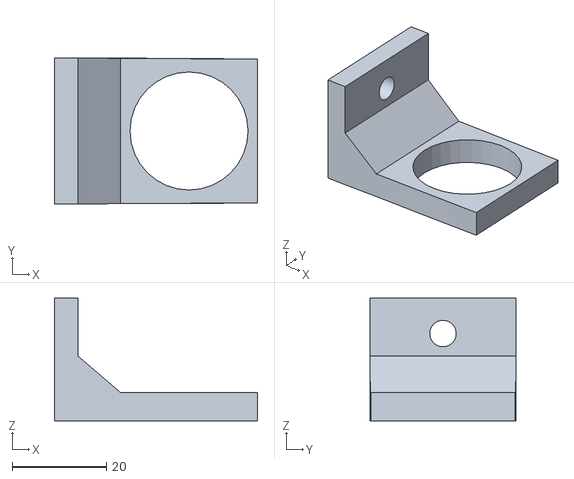
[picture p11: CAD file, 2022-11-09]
FreiBox_Assembling/STLfiles/SyringeHolder/Freibox_SyringeHolder.stl
43.0 x 31.0 x 26.0

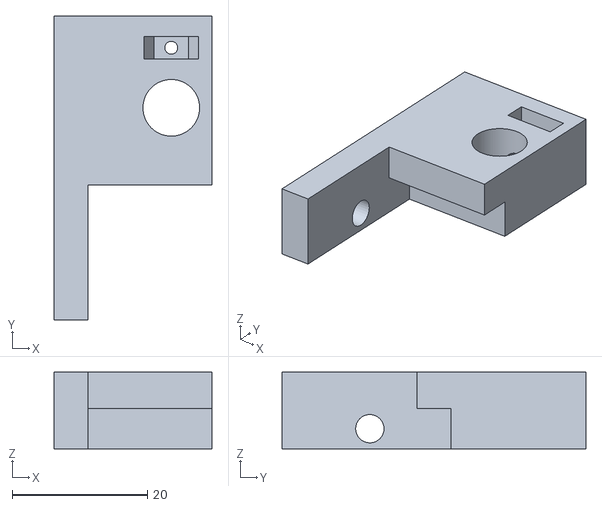
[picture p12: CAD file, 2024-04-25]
MiniscopeHolder_FreiBox2022_delaCrompeBrice/HolderForMiniscopeV4_Brice _Part1_UPDATED.stl
23.3 x 45.0 x 11.4

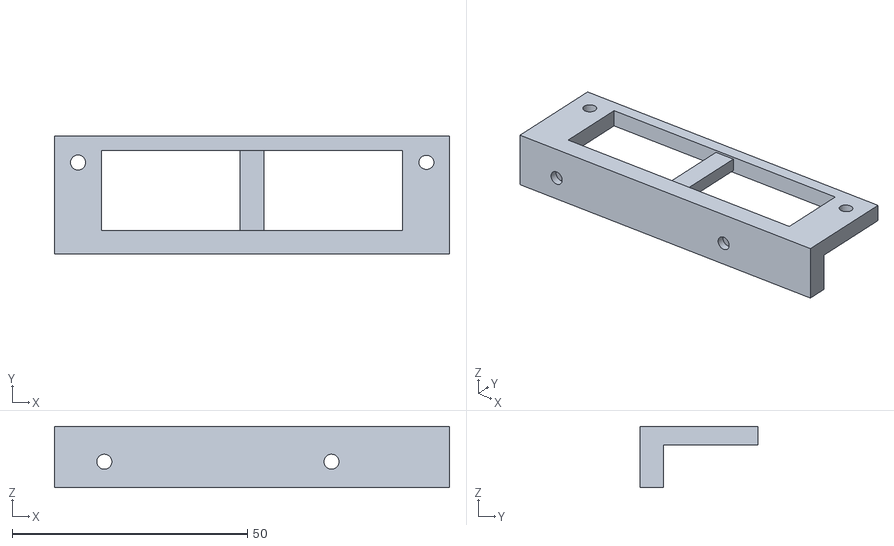
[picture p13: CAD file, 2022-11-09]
FreiBox_Assembling/STLfiles/ArduinoHolder/Freibox_ArduinoHolder_Part2.stl
83.9 x 25.0 x 13.0

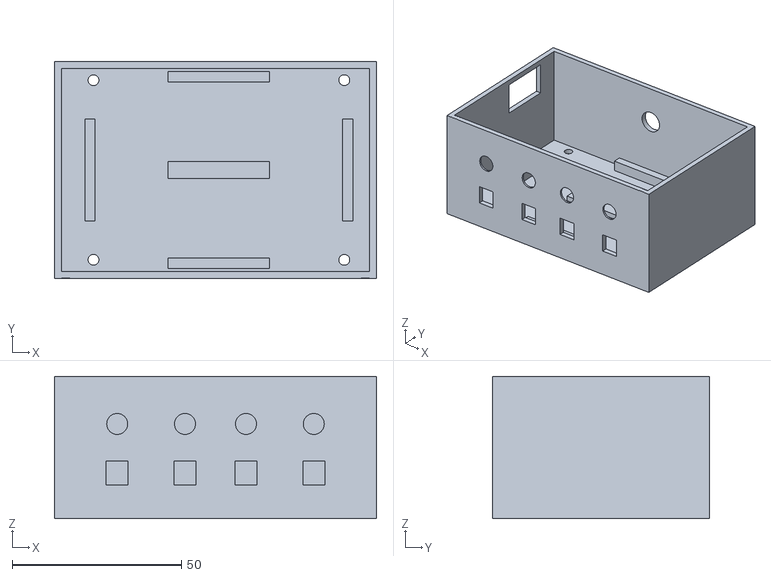
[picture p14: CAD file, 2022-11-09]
FreiBox_Assembling/STLfiles/AuditoryBox/Freibox_AuditoryBox_Part1.stl
95.0 x 64.0 x 42.0

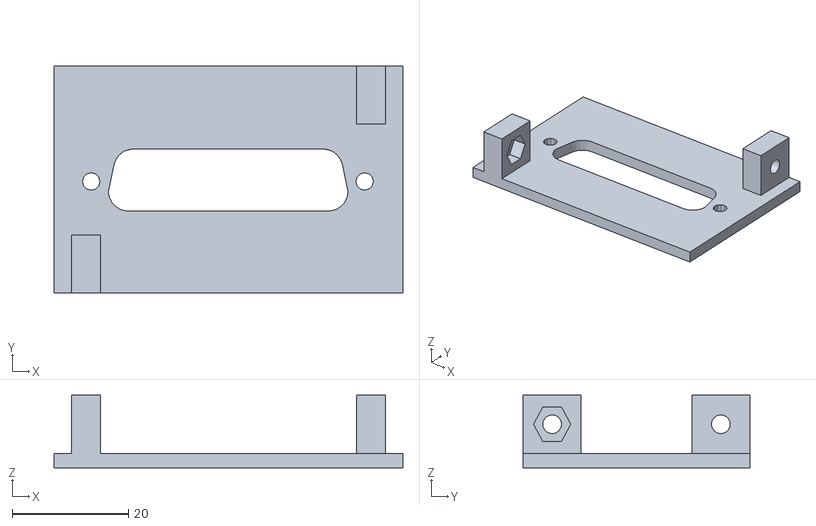
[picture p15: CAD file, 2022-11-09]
FreiBox_Assembling/STLfiles/CableBox/Freibox_InsideBox_Rear.stl
60.0 x 39.0 x 12.5

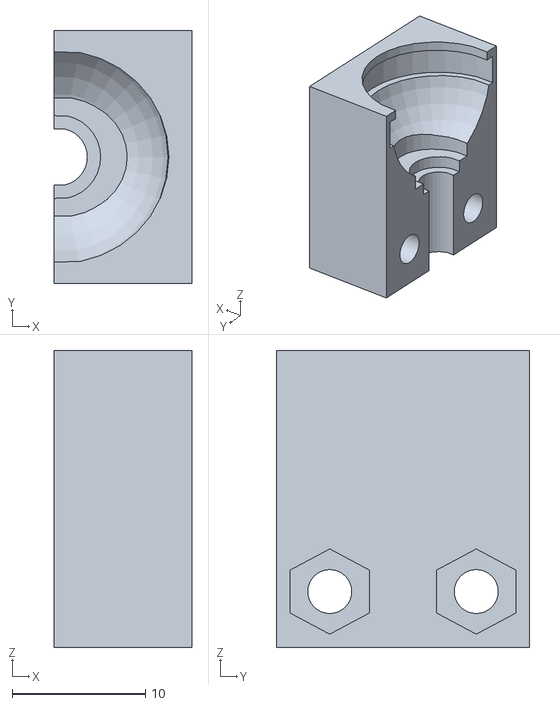
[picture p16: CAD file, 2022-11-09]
FreiBox_Assembling/STLfiles/LEDholder/Freibox_LEDholder_Part2.stl
10.4 x 19.0 x 22.3

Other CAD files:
FreiBox_Assembling/STLfiles/ElectronicBox/Freibox_ElectronicBox_Rear.stl
FreiBox_Assembling/STLfiles/LickingChamber/Freibox_LickingChamberGate_motorHolder_Part2.stl
FreiBox_Assembling/STLfiles/LickingSpoutHolder/Freibox_LickingSpoutHolder_pipeSecuringConnector.stl
MiniscopeHolder_FreiBox2022_delaCrompeBrice/HolderForMiniscope_v4_Part2.stl
FreiBox_Assembling/STLfiles/ElectronicBox/Freibox_ElectronicBox_Ground.stl
FreiBox_Assembling/STLfiles/ElectronicBox/Freibox_ElectronicBox_Left.stl
FreiBox_Assembling/STLfiles/ElectronicBox/Freibox_ElectronicBox_Right.stl
FreiBox_Assembling/STLfiles/ElectronicBox/Freibox_ElectronicBox_top.stl
FreiBox_Assembling/STLfiles/LickingChamber/Freibox_LickingChamberGate_LickingChamber.stl
FreiBox_Assembling/STLfiles/LickingChamber/Freibox_LickingChamberGate_MotorGear.stl
FreiBox_Assembling/STLfiles/LickingChamber/Freibox_LickingChamberGate_gate.stl
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

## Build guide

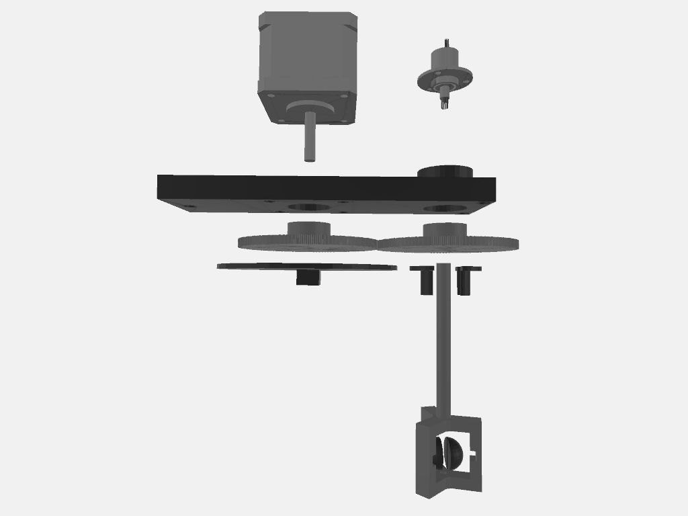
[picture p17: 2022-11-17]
Commutator_FreiBox2022/PublishedDesign/FreiBoxActiveCommutator_Assembly.tiff

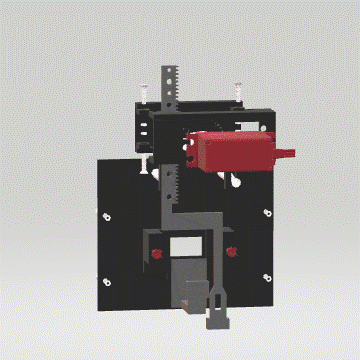
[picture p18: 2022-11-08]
FreiBox_Assembling/GIF/FreiBox_Assembling_LickingChamber.gif

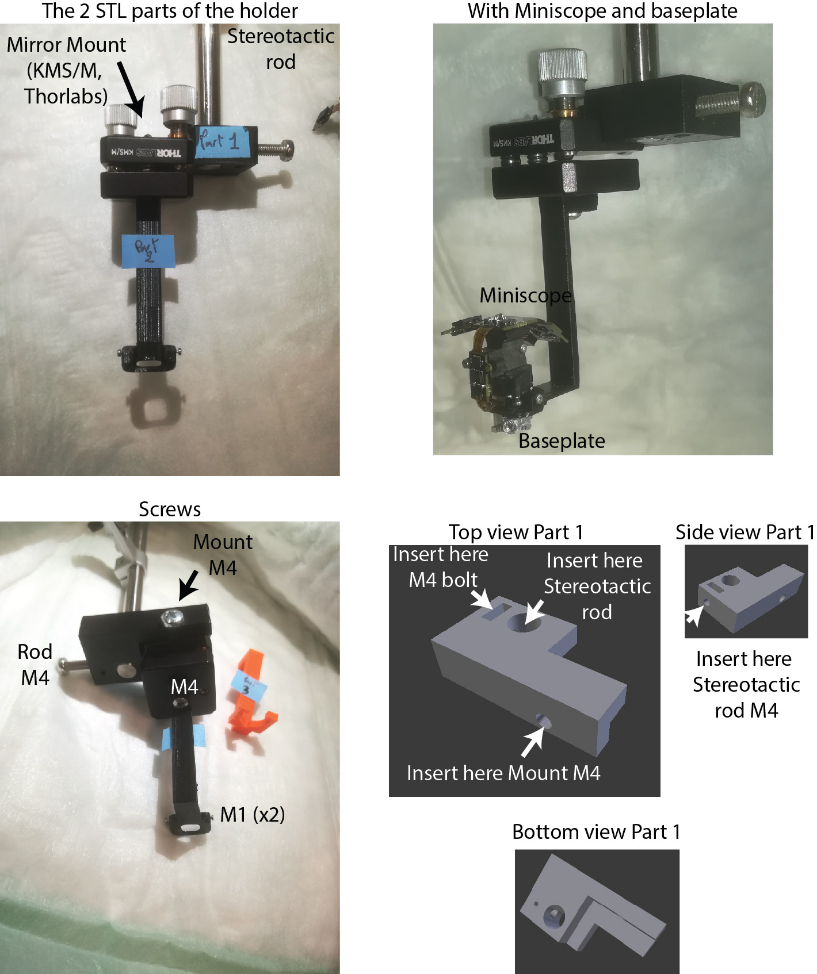
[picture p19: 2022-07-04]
MiniscopeHolder_FreiBox2022_delaCrompeBrice/MiniscopeV4Holder_Assemblage.jpg

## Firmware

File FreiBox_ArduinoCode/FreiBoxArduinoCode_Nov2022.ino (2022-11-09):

// FreiBox code Nov 2022
// This code version includes:
// - Reward probability
// - Laser driving + masking LED
// 
// Overflow for micro = 71.6 minutes (2^32 / 1000000 / 60 = 71.6 minutes) => Reset button
#include <DIO2.h>
#include <Servo.h> 

//Input pins
const GPIO_pin_t ENTER_LICK_CHAMBER = DP31;
const GPIO_pin_t ENTER_NOSE_POKE = DP29;
const GPIO_pin_t LICK_RIGHT = DP3;
const GPIO_pin_t LICK_LEFT = DP2;

//Output pins
const int AUDITORY_CUE = 4; 
const GPIO_pin_t WATER_DELIVERY_RIGHT = DP51;
const GPIO_pin_t WATER_DELIVERY_LEFT = DP49;
const GPIO_pin_t LICK_CHAMBER_LIGHT = DP10; 
const GPIO_pin_t NOSE_POKE_PORT_LIGHT = DP11; 
const GPIO_pin_t LED3 = DP9; // Masking LED 
const GPIO_pin_t LED4 = DP8; // Not used, was 46
const GPIO_pin_t LASER_PIN = DP6;
const GPIO_pin_t MASKING_LED_TRIGGER = DP36;  // NEW
const GPIO_pin_t SYNC = DP7;
    
// For Servo
const byte interrupt_pin = 21;
const int servo_control_pin = 5;

// Imported Session parameters
int BLOCK_NUMBER = 0;
int BLOCK_LENGTH = 0;
int FIRST_BLOCK = 0; //Correct licking spout: 0=Right // 1= LEFT
int reward_prob = 0;
bool reward_bool = false; 

// Imported Epoch Duration
unsigned long ITI_DURATION;
unsigned long TIME_NOSEPOKE_TO_OPEN_GATE;
unsigned long WALKING_WINDOWS_DURATION;
unsigned long RESPONSE_WINDOWS_DURATION; 
unsigned long WAITING_ANTICIPATION; 
unsigned long POST_REWARD_WAITING;
unsigned long LASER_TIME; //1 = walking, 2 = response, 12 = walking and response, 3 = anticipation, 4 = post reward, 34 = anticipation and post reward
// Laser probability
long laser_random = 0;        //will be changed to a random number each trial
bool laser_on_bool = false;   //boolean if this trial will have a laser activation
int LASER_PROBABILITY;
int LASER_BLOCK;
int laser_this_block = 0;

// Imported 'Hardware' parameters
int number_licks_for_hit = 3;
int delay_between_licking_reading = 50; //in msec 
int pump_opening_time = 20; //in msec
int RESPONSE_CUE = 5000; // in Hz

// Behavioral results
int OMISSION = 0;
int HIT_LICKING = 0;
int MISS_LICKING = 0;
int ERROR_LICKING = 0;
int mouse_left_nose_poke_port = 0; // this will go 1 once mouse left nose poke port and we have saved that time stamp. after that we are no longer interested in nose poke port => To suppress (local only !!!)
unsigned long laser_on_time = 0;
unsigned long laser_off_time = 0;

//Max time: 70 min to avoid data and clock overflow
unsigned long max_time = 65 * 60 * 1000000; //up to 70 min in micro s
int max_block_length;

//Variable to check before each new trial whether we will hit the max time
unsigned long time_before_new_trial;

// Recording Arrays
const int lick_array_length = 100; //down from 100 = 5s max of recording with 50msec delay

// Exported licking array
unsigned long lick_array[lick_array_length];
unsigned long lick_array_Error[lick_array_length];
unsigned long lick_array_correct_spout_Anticipation[lick_array_length];
unsigned long lick_array_incorrect_spout_Anticipation[lick_array_length];
unsigned long lick_array_correct_spout_PostReward[lick_array_length];
unsigned long lick_array_incorrect_spout_PostReward[lick_array_length];

// Exported Head detection array
unsigned long chamber_leave_array_response_window[lick_array_length];
unsigned long chamber_leave_array_anticipation[lick_array_length];
unsigned long chamber_leave_array_post_reward[lick_array_length];

// exported Time variables to python
unsigned long session_start_time = 0;
unsigned long session_end_time = 0;
unsigned long light_on_time = 0;
unsigned long enter_nose_poke_port_time = 0;
unsigned long leave_nose_poke_port_time = 0;
unsigned long enter_lick_chamber_time = 0;
unsigned long omission_time = 0;
unsigned long auditory_cue_time = 0;
unsigned long error_time = 0;
unsigned long miss_time = 0;
unsigned long hit_time = 0; 
unsigned long reward_delivery_time = 0;
unsigned long trial_end = 0;
unsigned long python_transfer_start_time = 0;
unsigned long python_transfer_end_time = 0;

unsigned long gate_opening_time = 0; 

// exported Variables from Function

int licking_result_w_lick_number = 0;

//white noise
const int white_noise_values_number = 1000;
int rand_array[white_noise_values_number];

int licking_block_type = 0;
int licking_block_type_output = 0;

int time_out = 0;
int time_outDuration = 4000;

// Gate Control
Servo myServo; // create the servo object
int max_position_closing = 100; //Full counter-clockwise
int max_position_opening = 170; //Full clockwise
int servo_closing_speed = 50; // Delay in usec
int opening_stop = 0;
int emergency_opening = 0;

//Performance measure fo block changes
int OMISSION_WITHIN_BLOCK = 0;
int FILTERED_TRIAL_WITHIN_BLOCK_COUNTER = 0;
int TOTAL_TRIAL = 0;
int FIRST_TRIAL = 0;
int HIT_INTRA_BLOCK_COUNTER = 0;
int TOTAL_TRIAL_WITHIN_BLOCK_COUNTER = 0;
int finished_blocks = 0;
int moving_window_size = 20;
const int hit_array_total_size = 100;
int hit_array[hit_array_total_size];
float moving_average;
int current_index_hit_array = 0;
int change_block = 0;

//Parameters for training
int trainingStage=0;
int ignoreTheIncorrectSpout = 0; //To avoid TTL detection of removed spout (=incorrect)
int breakLickingDetection_Hit = 0; //For flexible licking response window
int breakLickingDetection_Error = 0; //For flexible licking response window
int trainingWithoutNosePoke = 0; // No Nose poking
int gate_closes_directly_after_error= 0; 

//Parameters for pulses signal encoding behavioral events (block type, trial outcome...) 
int interPulseInterval=200; // InterPulses interval in microsec

// ======================================== //   
void setup(){
// ======================================== //
memset(hit_array,-1,sizeof(hit_array));
// Fill array with 0
memset(lick_array,0,sizeof(lick_array));
memset(lick_array_Error, 0, sizeof(lick_array_Error));
memset(lick_array_correct_spout_Anticipation,0,sizeof(lick_array_correct_spout_Anticipation));
memset(lick_array_incorrect_spout_Anticipation,0,sizeof(lick_array_incorrect_spout_Anticipation));
memset(chamber_leave_array_anticipation,0,sizeof(chamber_leave_array_anticipation));
memset(chamber_leave_array_response_window,0,sizeof(chamber_leave_array_response_window));
memset(lick_array_correct_spout_PostReward,0,sizeof(lick_array_correct_spout_PostReward));
memset(lick_array_incorrect_spout_PostReward,0,sizeof(lick_array_incorrect_spout_PostReward));
memset(chamber_leave_array_post_reward,0,sizeof(chamber_leave_array_post_reward));

Serial.begin(38400);

//declare pins

pinMode(AUDITORY_CUE, OUTPUT);
pinMode2f(WATER_DELIVERY_RIGHT, OUTPUT);
pinMode2f(WATER_DELIVERY_LEFT, OUTPUT);
pinMode2f(NOSE_POKE_PORT_LIGHT, OUTPUT);
pinMode2f(LICK_CHAMBER_LIGHT, OUTPUT);
pinMode2f(LED3, OUTPUT);
pinMode2f(LED4, OUTPUT);
pinMode2f(LASER_PIN, OUTPUT);
pinMode2f(SYNC, OUTPUT);
pinMode2f(MASKING_LED_TRIGGER, OUTPUT);  // NEW
pinMode2f(ENTER_LICK_CHAMBER, INPUT_PULLUP);
pinMode2f(ENTER_NOSE_POKE, INPUT_PULLUP);
pinMode2f(LICK_RIGHT, INPUT_PULLUP);
pinMode2f(LICK_LEFT, INPUT_PULLUP);
digitalWrite2f(LICK_CHAMBER_LIGHT, LOW);
digitalWrite2f(NOSE_POKE_PORT_LIGHT, LOW);
digitalWrite2f(LED3, LOW);
digitalWrite2f(LED4, LOW);
digitalWrite2f(SYNC, LOW);
digitalWrite2f(LASER_PIN, LOW);
digitalWrite2f(MASKING_LED_TRIGGER, LOW);  // NEW

make_frequencies_for_white_noise(white_noise_values_number);


// For Servo gate
myServo.attach(servo_control_pin);
pinMode(interrupt_pin, INPUT_PULLUP);
attachInterrupt(digitalPinToInterrupt(interrupt_pin), open_gate, CHANGE);
close_gate(servo_closing_speed); // close gate completely at beginning

randomSeed(analogRead(A0));

}

// ======================================== //
void loop()
{
// ======================================== // 
// Think about catch trials (same protocol without Cue)
while(FIRST_TRIAL == 0) // things we only need to do once, at the very beginning of a session    
     {  
     FIRST_TRIAL++; // Increment by 1 TOTAL_TRIAL to avoid infinite loop
     define_python_variables(); // get parameters from python GUI    
     max_block_length = BLOCK_LENGTH * 5; // To avoid infinite block length (important if an optogenetic effect occurs)    
     close_gate(servo_closing_speed); // close gate completely at beginning    
     session_start_time = micros();    
     pulses_signal(SYNC,10, 1); //Session start          
     
     if(trainingStage > 0)
       {
       defineTrainingParameters(trainingStage);
       }   
    
     licking_block_type = FIRST_BLOCK; // determine which spout is correct in this first block
     //licking_block_type_output = licking_block_type; //for debugging
     // determine if first block will be laser block
     if((LASER_BLOCK == 1) ||(LASER_BLOCK==12)||(LASER_BLOCK==123)||(LASER_BLOCK==1234))
       {
       laser_this_block = 1;
       }
     }     

// 0. Trial preparation: check if we still need more trials (block number and max ssssion time)
while((finished_blocks < BLOCK_NUMBER) && (time_before_new_trial < max_time))   
     { 
      // Resetting of all exported variables
      reset_exported_variables();
      // Pulses for recordings
      pulses_licking_block(licking_block_type); //Trial start         
    //A: Laser probability - for each trial, generate a random number (laser_random) which define if the laser is ON or OFF during the trial (laser_on_bool)
      laser_random = random(100);// make a random number that determines if we use laser this trial or not (in case that it is random)
      if(laser_random >= 100-LASER_PROBABILITY) //randomly choosing if the trial was a laser trial or not
        {      
        laser_on_bool = true;
        }
      else
        { 
        laser_on_bool = false;
        }
      //B: Reward probability  /////// NEW ////////////
     int  reward_random = random(100);
      if(reward_random <= reward_prob)
        {      
        reward_bool = true;
        }
      else
        { 
        reward_bool = false;
        }
      

// 1. ITI and Gate opening
 
      ITI_function(ITI_DURATION); // ITI
      
      // if mouse has nose in nose poke port before trial start, this waits until it comes out of port
      wait_for_no_beam_breaking_nose_poke_port(50);
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

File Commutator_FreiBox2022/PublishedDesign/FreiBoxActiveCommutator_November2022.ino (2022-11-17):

 /* Brice de la Crompe (Optophysiology lab / Diester lab) - Nov 2022
  * 
  *   Configuration 3 Hall sensors  (A, B and C)
  *   Their magnetic field define 6 different area (60 degrés)
  *   rotational adjustment in area 3 and 4 only
  *   Example of the measurment of the 'directionnal field' for A sensor (DF): 
  *           DF(A) = [analogRead(A)-analogRead(C)]-[analogRead(A)-analogRead(B)] 
  *           DF(A) = analogRead(B)-analogRead(C)        
       => if DF(A)>0 <=> Magnet is more oriented toward B than C  
       => if DF(A)<0 <=> Magnet is more oriented toward C than B 
       => The orientation of the magnet is defined in the following decision matrix by using this calculation method for the 3 sensors simultaneously 
  * 
  * 
  * Configuration:                                 Decision Matrix:
  * 
                ---                                       1     2     3     4     5     6
               - A - (Yellow)                     DF(A)  >0    >0    >0    <0     <0    <0
                ---                                           
                                                  DF(B)  <0    <0    >0    >0     >0    <0      
               6  1                                     
             5      2                             DF(C)  >0    <0    <0    <0     >0    >0              
     ---       4* 3**     ---                                    
    - C -                - B -                              
     ---                  ---                                       
   (Blue)               (Brown)                                 

Called in the code *10 and **11 to define when to adjust the position (>10)

 */    
int stepPin=6;
int dirPin=7;
int sleepPin=5;
int MS3pin=3;
int MS2pin=2;
int MS1pin=1;

int stepNumberForAdjustement = 100*16;//67; before 50 // Nema 17 = 1.8degre/step, so 67 steps = 120.6 degrees (=2 areas)! 

int sensorPinA = A5;  
int sensorPinB = A4;
int sensorPinC = A3;

int sensorValueA;
int sensorValueB;
int sensorValueC;

int decisionValueA=0;
int decisionValueB=0;
int decisionValueC=0;  

int numReadings=2; // Number of reading for average
int magnetDirection; // 
int previousMagnetDirection;
int previousDirection;

int needAdjustment=0;
int stopCounter=0;
// ======================================== // 
void setup() 
{
Serial.begin(9600);

pinMode(sensorPinA, INPUT);
pinMode(sensorPinB, INPUT);
pinMode(sensorPinC, INPUT);

pinMode(stepPin, OUTPUT);
pinMode(dirPin, OUTPUT);

pinMode(sleepPin, OUTPUT);
pinMode(MS1pin, OUTPUT);
pinMode(MS2pin, OUTPUT);
pinMode(MS3pin, OUTPUT);

digitalWrite(sleepPin, LOW);
digitalWrite(MS1pin, HIGH);
digitalWrite(MS2pin, HIGH);
digitalWrite(MS3pin, HIGH);


readPositionFunction();
magnetDirection=decisionFunction(decisionValueA,decisionValueB,decisionValueC);

}

void loop()
{

while(needAdjustment==0)
     {
     Serial.println("CheckingLoop");
//     Serial.println(" ");
//     Serial.println(magnetDirection);
//     Serial.print(" ");
//     Serial.print(magnetDirection);
//     Serial.println(" ");

   
     //delay(100);
     if(magnetDirection<10)
       {
       previousMagnetDirection=magnetDirection;
            
       }
     readPositionFunction();
     magnetDirection=decisionFunction(decisionValueA,decisionValueB,decisionValueC);  
     if(magnetDirection >= 10)
      {
      needAdjustment=1;
      digitalWrite(sleepPin, HIGH);
      break;
      }

   
///*     
   //   Serial.print("loop");
     Serial.print(" ");
     Serial.print(sensorValueA);
     Serial.print(" ");
     Serial.print(sensorValueB);
     Serial.print(" ");
     Serial.print(sensorValueC);     
     Serial.println(" ");
//*/     
     Serial.println("CheckingLoop");

 


   

     }
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

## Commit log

2022-07-04 Create Assembly instructions
2022-07-04 Update Assembly instructions
2022-11-08 Add files via upload
    Instruction to assemble the licking chamber
2022-11-08 Create assembling GIF
